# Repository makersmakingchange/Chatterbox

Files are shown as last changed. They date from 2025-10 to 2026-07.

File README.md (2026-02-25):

<!--- Open Source Assistive Technology: GitHub Readme Template Version 1.2 (2024-May-27)  --->

<!--- INSTRUCTIONS --->
<!--- This is a markdown template for creating the README.md file in a GitHub repository. This file is rendered and displayed automatically when someone visits the repository.

This document includes helper text that will not be displayed when rendered. Any text between the less-than sign + exclamation mark + three hyphen-minus (<!---) and matching three hyphen-minus + greater-than sign will not be displayed. This helper text can be deleted once the corresponding section is completed.

This template has a number of fields that can be searched and replaced with other text:
 - <Device_Name> Replace this with filename-friendly version of the device with underscores. e.g., Open_Wobble_Switch
 - <DeviceName> Replace this with the human-readable name of the device with spaces. e.g., Open Wobble Switch
 - <DesignerName> Replace this with the person or organization responsible for the design. e.g., John Doe.
 - <Repository_Link> Replace this with the web address for the repository. e.g., (e.g., https://github.com/makersmakingchange/Open-Wobble-Switch))
 - <MMCWebLink> This is the website address including an alphanumeric id for the Makers Making Change Website. e.g., 01tJR000000698oYAA. This will come from MMC staff.  
 - <MaterialCost> Replace this with the dollar cost and currency (CAD, USD, etc.) of the materials of the device.
 - <ShippingCost> Replace this with the dollar cost and currency (CAD, USD, etc.) of shipping the device (if possible).
 - <YEAR> year(s) of the copyright
 
Any text that is currently holding a space / is an instruction for the person filling in the README is in all capitals, to make it easier to see them in a rendered version.

--->
 
<!--- TITLE --->
# Chatterbox

## Overview
<!--- A brief summary of the project. What it does, who it is for, how much it costs. --->
The Chatterbox is an Augmented and Alternative Communication (AAC) device that allows users to play pre-recorded messages using single or dual switch scanning. The Chatterbox provides auditory and visual feedback to indicate the message a user can play. 

The Chatterbox is comprised of off-the-shelf electronics and 3D printed parts. 

The Chatterbox is open assistive technology (OpenAT). Under the terms of the open source licenses, the device may be built, used, and improved upon by anyone.

The overall cost of materials is about $135 CAD.

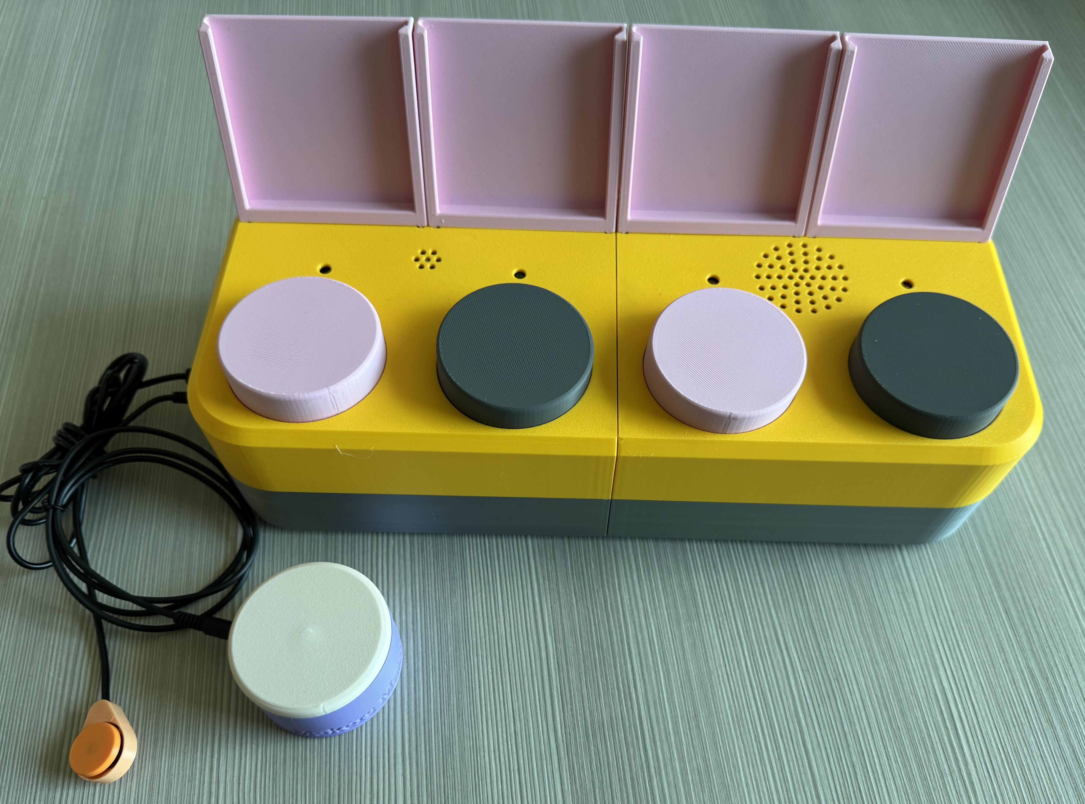
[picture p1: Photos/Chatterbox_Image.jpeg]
Picture of the Chatterbox.


## Makers Making Change Assistive Device Library
<MMCWebLink>

## How to Obtain the Device
### 1. Do-it-Yourself (DIY) or Do-it-Together (DIT)

This is an open-source assistive technology, so anyone is free to build it. All of the files and instructions required to build the device are contained within this repository. Refer to the Maker Guide below.

### 2. Request a build of this device

You may also submit a build request through the [Makers Making Change Assistive Device Library Listing](<MMCWebLink>) to have a volunteer maker build the device. As the requestor, you are responsible for reimbursing the maker for the cost of materials and any shipping.

### 3. Build this device for someone else

If you have the skills and equipment to build this device, and would like to donate your time to create the device for someone who needs it, visit the [MMC Maker Wanted](https://makersmakingchange.com/maker-wanted/) section.

## Build Instructions
<!--- Outline the major steps required to create a build --->

### 1. Read through the Maker Guide

The [Maker Guide](/Documentation/Chatterbox_Maker_Guide.pdf)  contains all the necessary information to build this device, including tool lists, assembly instructions, programming instructions (if applicable) and testing.

### 2. Order the Off-The-Shelf Components

The [Bill of Materials](/Documentation/Chatterbox_BOM.xlsx) lists all of the parts and components required to build the device.

### 3. Order the custom PCBS

The [PCB Files](/Build_Files/PCB_Build_Files) contain the Gerber files needed to order the PCBs, and instructions on how to order them can be found in the [Maker Guide](/Documentation/Chatterbox_Maker_Guide.pdf).

### 4. Print the 3D Printable components

All of the files and individual print files can be found in the [/Build_Files/3D_Printing_Files](/Build_Files/3D_Printing_Files/) folder.

### 5. Assemble the Chatterbox

Reference the Assembly Guide section of the [Maker Guide](/Documentation/Chatterbox_Maker_Guide.pdf) for the tools and steps required to build the device.

## How to improve this Device
As open source assistive technology, you are welcomed and encouraged to improve upon the design. 

## Files
### Documentation
<!--- Update the name, link, and version for documentation --->
| Document             | Version | Link |
|----------------------|---------|------|
| Design Rationale     | 1.0     | [Chatterbox_Design_Rationale](/Documentation/Chatterbox_Design_Rationale.pdf)     |
| Maker Guide          | 1.0     | [Chatterbox_Maker_Guide](/Documentation/Chatterbox_Maker_Guide.pdf)     |
| Bill of Materials    | 1.0     | [Chatterbox_Bill_of_Materials](/Documentation/Chatterbox_BOM.xlsx)     |
| User Guide           | 1.0     | [Chatterbox_User_Guide](/Documentation/Chatterbox_User_Guide.pdf)    |
| Changelog            | 1.0     | [Changelog](CHANGES.txt)     |

### Design Files
<!--- Include a copy of the original design files to facilitate easy editing and customization. Consider also including a generic format (e.g., STEP) --->
 - [CAD Files](/Design_Files/CAD_Design_Files)
 - [PCB Files](/Design_Files/PCB_Design_Files)

### Build Files
<!--- Include a copy of the build files intended for manufacturing. This may include svg files for laser cutting, stl files for 3d printing, Gerber files for custom PCBs, and Arduino files for custom firmware. --->
 - [3D Printing Files](/Build_Files/3D_Printing_Files)
 - [PCB Build Files](/Build_Files/PCB_Build_Files)
 - [Firmware Files](/Build/Firmware_Files)

## License
<!--- Add the year(s) for the copyright and the Designer Name. You may use the standard set of open licenses or choose your own for the hardware, software, and accompanying materials. --->
Copyright (c) 2025, Neil Squire.

This repository describes Open Hardware:
 - Everything needed or used to design, make, test, or prepare the Chatterbox is licensed under the [CERN 2.0 Weakly Reciprocal license (CERN-OHL-W v2) or later](https://cern.ch/cern-ohl ) .
 - All software is under the [GNU General Public License v3.0 (GPL-3.0)](https://www.gnu.org/licenses/gpl.html).
 - Accompanying material such as instruction manuals, videos, and other copyrightable works that are useful but not necessary to design, make, test, or prepare the <Device-Name> are published under a [Creative Commons Attribution-ShareAlike 4.0 license (CC BY-SA 4.0)](https://creativecommons.org/licenses/by-sa/4.0/) .

You may redistribute and modify this documentation and make products using it under the terms of the [CERN-OHL-W v2](https://cern.ch/cern-ohl).
This documentation is distributed WITHOUT ANY EXPRESS OR IMPLIED WARRANTY, INCLUDING OF MERCHANTABILITY, SATISFACTORY QUALITY AND FITNESS FOR A PARTICULAR PURPOSE.
Please see the CERN-OHL-W v2 for applicable conditions.

Source Location: [Chatterbox Repository](https://github.com/makersmakingchange/Chatterbox)

## Attribution
<!--- Provide any necessary attribution for designs or components that are included in the device or as part of the project. --->
The device was designed by Stephan Dobri for Neil Squire. It was based on the [Open Playback Recorder](https://github.com/makersmakingchange/Open-Playback-Recorder), from Neil Squire.

<!--- This is the attribution for the template. --->
The documentation template was created by Makers Making Change / Neil Squire Society and is used under a CC BY-SA 4.0 license. It is available at the following link: [https://github.com/makersmakingchange/OpenAT-Template](https://github.com/makersmakingchange/OpenAT-Template)

### Contributors
<!--- List the names of the people that contributed to the design. This could include the original source of the idea, designers, testers, documenters, etc. --->
Designers:
 - Stephan Dobri
 - Jake McIvor

Feedback providers:
- [SpikedCola](https://github.com/SpikedCola)

Testers:
 - Surrey School AAC Team
 - SET-BC
 - Augmented and Alternative Communication - Interaction and Technology Lab (AAC-IT) at Queen's University

---

<!-- ABOUT MMC START -->
## About Makers Making Change
[Makers Making Change Logo](https://www.makersmakingchange.com/)

Makers Making Change is a program of [Neil Squire](https://www.neilsquire.ca/), a Canadian non-profit that uses technology, knowledge, and passion to empower people with disabilities.

Makers Making Change leverages the capacity of community based Makers, Disability Professionals and Volunteers to develop and deliver affordable Open Source Assistive Technologies.

 - Website: [www.MakersMakingChange.com](https://www.makersmakingchange.com/)
 - GitHub: [makersmakingchange](https://github.com/makersmakingchange)
 - Bluesky: [@makersmakingchange.bsky.social](https://bsky.app/profile/makersmakingchange.bsky.social)
 - Instagram: [@makersmakingchange](https://www.instagram.com/makersmakingchange)
 - Facebook: [makersmakechange](https://www.facebook.com/makersmakechange)
 - LinkedIn: [Neil Squire Society](https://www.linkedin.com/company/neil-squire-society/)
 - Thingiverse: [makersmakingchange](https://www.thingiverse.com/makersmakingchange/about)
 - Printables: [MakersMakingChange](https://www.printables.com/@MakersMakingChange)

### Contact Us
For technical questions, to get involved, or to share your experience we encourage you to [visit our website](https://www.makersmakingchange.com/) or [contact us](https://www.makersmakingchange.com/s/contact).
<!-- ABOUT MMC END -->

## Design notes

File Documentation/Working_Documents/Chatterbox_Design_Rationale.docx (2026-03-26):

# Overview

The Chatterbox is a switch scanning communication device which provides auditory feedback to guide the user while scanning. The Design Rationale is intended to provide designers and maker information about the design process and design decisions behind the development of the Chatterbox.

Figure 1: The completed Chatterbox with assistive switches.

The Design Rationale details development chronologically. For full details on the current published version of the device, you may skip to the Detailed Design section.

# Introduction

The request for this device came from staff at a Surrey School District school for students with disabilities. The staff were looking for an affordable device to help students with visual impairment learn switch scanning for communication devices. The goal of the device is to help students trial switch scanning communication devices before purchasing a more expensive commercial option. The device requires auditory feedback as it is intended for users with visual impairment, and many commercially available options use visual feedback for switch scanning.

The device allows users to record their own messages to play back when selected using switch scanning, or direct selection of a message. Messages can range from single words to full sentences or sections of songs. The messages allow users who have complex communication needs to interact with other people and participate in group activities. The simplicity of the device helps teach users about switch scanning, before using more complex switch scanning communication devices.

The device is intended for users with complex communication needs and visual impairments, including users who are deaf-blind, blind, visually impaired, or have cerebral palsy (CP).

# Requirements

## Problem Statement

Design an OpenAT device that enables a user with visual impairment to perform switch-enabled auditory scanning.

## User Needs

G01 | A switch scanning communication device that uses auditory feedback for switch scanning.
G02 | Device is simple to help teach users how to switch scan rather than learning how to use the device.
G03 | Has integrated switches to directly play and record messages.
G04 | The device can do single and perhaps dual switch scanning.
G05 | The volume of the device can be controlled.
G06 | The delay between scanning messages can be controlled.
G07 | The device can hold images on paper near each switch to represent the message.
G08 | The device can record and play at least three messages.
G09 | The device is more affordable than current commercially available options.
G10 | The device is small enough to fit on a user’s lap tray.
G11 | The device has different message levels to store and playback sets of messages.
G12 | The device shows which level it is on.
G13 | The device shows which message is being played/recorded.
G14 | The device must be able to clean.
G15 | Integrated buttons should not be angles
G16 | It should be easy to record messages.

## Functional Requirements

F01 | Secondary users must be able to record their own messages.
F02 | Messages up to a minute in length must be possible to record.
F03 | The device must record at least three separate messages.
F04 | The device must work with single switch scanning.
F05 | Users must be able to add message labels or pictures to help identify the messages (76x76 mm minimum size).
F06 | The delay between messages while switch scanning can be modified.
F07 | The volume of the playback must be adjustable by a secondary user.
F08 | The device must be able to be cleaned with a damp cloth.
F09 | The device must fit on a student’s lap tray (maximum length 330 mm).
F10 | The device must be able to record and play at least two different levels of messages.
F10a | The device must have a means to change the level.
F10b | The device must have a way to indicate the current level.
F11 | Integrated buttons on the device must be parallel to the surface the device is mounted or placed upon.
F12 | The device enables switch-enabled auditory scanning
F12a | The device plays pre-recorded messages when triggered by primary user.
F12b | The device must be able to record a message for each position.
F12c | The device must have a visual indicator for each position.
F12d | The device must have a means for indicating the current position.
F12e | The device must play a selected message again when selected by the user.
F13 | The device must have a way to indicate which position is being recorded.

## Evaluation Criteria

NF01 | The device should have separate jacks for connecting external assistive switches for direct access.
NF02 | The device should provide an option for two-switch scanning.
NF03 | The device should have integrated buttons for direct access
NF04 | The device should have visual feedback for secondary users, or users with partial vision.
NF05 | The device should have the option to have integrated buttons with different tactile tops.

## Constraints

C01 | The device must cost less than other commercially available options ($300 CAD).
C02 | The device must be makeable by a volunteer.
C03 | Any required custom printed circuit boards (PCBs) are makeable through low-volume prototyping services.
C04 | The device design must be licensed as open source hardware.

# Research

Research on existing devices was conducted between September 10th and 18th, 2024. Research was conducted by searching Google for “auditory scanning devices”, “switch scanning devices”, and using “DIY”, and “homemade” with the previous searches. The augmented and alternative communication (AAC) team that requested this device also suggested commercially available devices as starting points for the design.

## Background

Simple switch scanning AAC devices are used by people with complex communication needs and limited motor function. Messages are often short (single words or short statements), but may be longer depending on the user’s needs and the context of the use.

## Commercially Available Options

Options that can be purchased but not made by a maker.

### AbleNet Inc. Talking Brix 2

Title / Name of device | Talking Brix 2
Link | https://www.ablenetinc.com/talkingbrix-2/
Author | AbleNet Inc.
License | N/A
Cost | $365.00 CAD

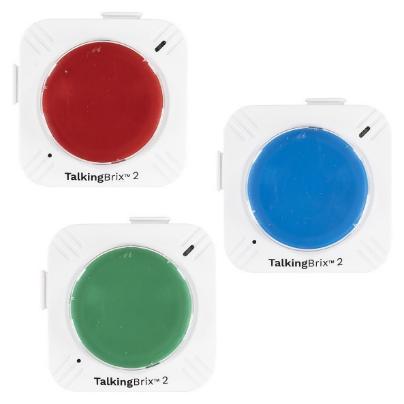
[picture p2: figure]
Three AbleNet Talkig Brix. They are white squares with indicator lights and a circular red, green, or blue button on them.

Figure 2: Set of three Talking Brix 2 devices.

The Talking Brix 2 come in sets of three individual playback buttons. Each button works separately, can record up to 10 seconds of audio, and have rechargeable batteries. To record messages, the user moves a switch on the bottom of the base to “Rec” and holds the Brix button down while recording the message. When the switch is turned to “On”, the recorded message will play when the button is pressed. The Brix can be physically connected using the slots and tabs on the sides; however, these connections are for physical mounting only and each Brix will still need to be pressed to be activated.

Requirements Met | Requirements Unmet
F01, F03 | F02, F04-F07

#### Useful Design Features

The tabs and slots on the sides of the Brix to connect them are well made. There are also push pins on the tabs which appear to be useful for creating electrical communication among the Brix, although they are unused in this design.

Each Brix has a magnet in the bottom to allow for mounting on metal surfaces.

### Cheap Talks 4 & 8 – Direct Scan and Jacks

Title / Name of device | Cheap Talks 4 & 8 – Direct Scan and Jacks
Link | https://enablingdevices.com/product/cheap-talks-4-8-direct-scan-jacks/
Author | Enabling Devices
License | N/A
Cost | $319.95 – $339.95 (USD)

Figure 3: Cheap Talks 4 - Direct Scan and Jacks

The Cheap Talks 4 & 8 – Direct Scan and Jacks can record and replay either four (4) or eight (8) messages. Messages can be up to 37.5 seconds in length on each button. The device supports single or dual switch scanning with external switches in eight (8) scanning modes. Users can also press the buttons on the device to directly select one of the messages to play.

Users record messages by holding the “Record” button and intended message button down simultaneously. Dials and buttons on the back allow users to change the volume, scanning speed, and scanning mode.

Requirements Met | Requirements Unmet
F01, F03, F04, F07 | F02, F05, F06

#### Useful Design Features

Options of multiple scanning methods (https://enablingdevices.com/wp-content/uploads/2017/09/Scan-Modes.pdf) are useful and described well.

The buttons also light up when playing messages or other auditory cues for scanning.

### Talk 4 with Levels

Title / Name of device | Talk 4 with Levels
Link | https://enablingdevices.com/product/talk-4-wlevels/
Author | Enabling Devices
License | N/A
Cost | $299.95 (USD)

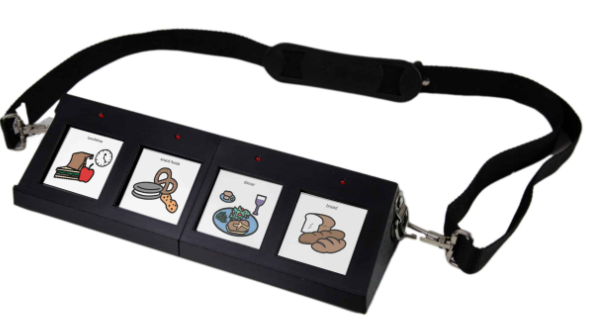
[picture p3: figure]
A black device with a lanyard and four buttons. The buttons are square and have images of types of food on them.

Figure 4: Talk 4 with Levels

The Talk 4 is like the Cheap Talks, but only has one jack for switch scanning. It is a more portable version, with 12 levels of messages, and up to 300 seconds of memory for recorded messages.

Requirements Met | Requirements Unmet
F01, F03, F04 | F02, F05-F07

#### Useful Design Features

Levels are useful for increasing the number of possible messages.

### Announcer with 6 Levels

Title / Name of device | Announcer with 6 Levels
Link | https://enablingdevices.com/product/announcer-w6-levels/
Author | Enabling Devices
License | N/A
Cost | $339.95 (USD)

Figure 5: Announcer with 6 Levels

The Announcer has six (6) levels of messages, with 300 seconds of message recording time. The Announcer has a built-in switch and mounting clamp, and can be activated with an external switch. The beginning of messages are played at a lower volume than the messages when selected/played back.

Requirements Met | Requirements Unmet
F01, F02, F03 | F04, F05-F07

#### Useful Design Features

Playing the message cue at a lower volume than the message may be useful.

### Tech Scan and Smart Scan Devices

Title / Name of device | Tech Scan and Smart Scan Devices
Link | https://www.turningpointtechnology.com/Comm/Auditory.asp
Author | Turning Point Technology
License | N/A
Cost | $1,018 - $2,450 USD

Figure 6: Tech Scan Device

The Tech Scan and Smart Scan devices are direct and switch scanning devices with different numbers of messages. The devices have either eight (8) or 32 messages/square for message selection. Each device also has multiple levels for more messages, and standard message length is 4.5 seconds.

Requirements Met | Requirements Unmet
F01, F03 | F02, F04, F05-F07

#### Useful Design Features

No new design features other commercially available options haven’t included.

### Talk About! Communicator

Title / Name of device | Talk About! Communicator
Link | https://www.adaptivetechsolutions.com/pd-talk-about-communicator/?srsltid=AfmBOoq3FJIaj412QSOrk76TpdaQk041moJlEOmOddBrGyGvxO57XSLE
Author | Adaptive Tech Solutions
License | N/A
Cost | $27.58-$37.83 (USD)

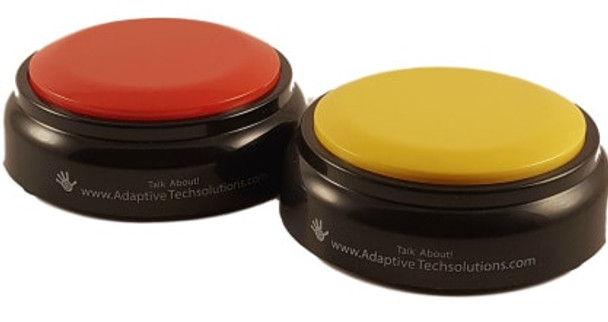
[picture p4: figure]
Talk About! Communication Talking Buttons

Figure 7: Two Talk About! Communicators

Records and plays back messages up to 20 seconds long. Includes non-slip pads on the bottom, and there is a switch jack version for use with external switches. Additionally has a belt clip so make it wearable/portable.

Requirements Met | Requirements Unmet
F01 | F02-F07

#### Useful Design Features

Can be used with an external switch, and option for belt clip is interesting.

### iTalk 4

Title / Name of device | iTalk 4
Link | https://www.ablenetinc.com/italk4/
Author | AbleNet, Inc.
License
Cost | $275 (USD)

Figure 8: iTalk 4 device

The iTalk 4 offers four individual messages with three message levels (12 messages total) with a total of six (6) minutes of recording time. Each button corresponds to a message, and each message can be recorded independently. External switches can be used for each message; however, there is not a switch scanning mode.

Requirements Met | Requirements Unmet
F01, F03 | F02, F04-F07

#### Useful Design Features

Individual recording of each message is useful, as are the levels.

### Compartmentalized Communicators

Title / Name of device | Compartmentalized Communicators
Link | https://enablingdevices.com/product/compartmentalized-communicators/?srsltid=AfmBOoqLPBpBhjRKIVVAHyzmXBPQkFkR4kDSdKowHBe27DFtp3_HjVcO
Author | Enabling Devices
License
Cost | $179.95 - $269.95 (USD)

Figure 9: Compartmentalized Communicators in 2, 3, and 4 compartment versions.

The Compartmentalized Communicator has two-, three-, or four-compartment versions. Each compartment can record up to a five (5) second message that is played back when the plate is pressed. There are spaces for images and objects to be placed above each compartment. There is no switch scanning option.

Requirements Met | Requirements Unmet
F01, F03, F07 | F02, F04-F06

#### Useful Design Features

Having space for both an object and an image may be useful.

Having the switches flat (not angled) makes it easier for some users to press.

## DIY / Maker-Friendly Options

Options that can be made by a maker.

### Partner – Assisted Auditory Scanning (PAAS)

Title | Partner – Assisted Auditory Scanning
Link | https://communication.bridgeschool.org/intervention/aac-system-design-guiding-principles/aac-system-design-examples-of-aac-tools-and-techniques/
Author | N/A
License | N/A
Cost | N/A
Test Build (Y/N) | N/A
Add to Library (Y/N) | N/A

Partner-Assisted Auditory Scanning relies on a partner going through a series of options verbally, and having the user select from the choices they present. The series of options can be developed by anyone, and can be presented in various ways (pictures, words, etc.).

Requirements Met | Requirements Unmet
None | F01-F07

### Open Playback Recorder

The Open Playback Recorder is an open-source device that can record three lists of voice messages that its user can playback via the trigger of an accessible button connected through a 3.5 mm mono jack. It aims to assist users with communication difficulties by giving them alternative methods to engage in conversation. This device has functionality like AbleNet’s Big Mack or Step by Step.

Title | Open Playback Recorder
Link | https://www.makersmakingchange.com/s/product/open-playback-recorder/01tJR000003DNOVYA4
Author | Neil Squire/Makers Making Changes
License | CERN OHL-W v2, GPL-3.0, CC BY SA 4.0
Cost | $90 (CAD)
Test Build (Y/N) | Y
Add to Library (Y/N) | Already in library

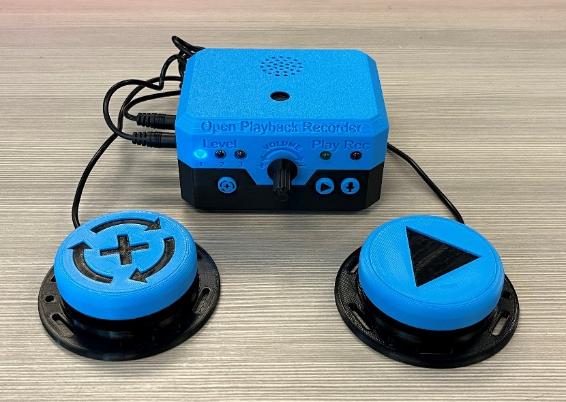
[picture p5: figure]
Picture of Open Playback Recorder.

Figure 10: Open Playback Recorder

The Open Playback Recorder allows users to record and switch scan messages to engage in communication. There are three levels to record different messages, and users record a series of messages on each level. Recording, switching levels, and scanning messages can all be done using assistive switches, or built-in switches on the device.

Messages cannot be modified or accessed directly; users must re-record all messages on a level at once, and must switch scan to access messages.

Requirements Met | Requirements Unmet
F01-F04, F07 | F05, F06

#### Useful Design Features

Most of the components and firmware from this device can be used as the basis for the Auditory Scanning Blocks device.

### Single Message Playback Switch

The Single Message Playback Switch is a switch adapted device that can store and play back a single 30 second message. The device can be used both as a toy or as a communication aid. A commercially available voice recording button is modified so that it can be activated using a secondary assistive switch with a 3.5 mm plug.

Title | Single Message Playback Switch
Link | https://www.makersmakingchange.com/s/product/single-message-playback-switch/01tJR000001HyonYAC
Author | Neil Squire/Makers Making Changes
License | CERN OHL-W v2, GPL-3.0, CC BY SA 4.0
Cost | $12.50 (CAD)
Test Build (Y/N) | Y
Add to Library (Y/N) | Already in library

Figure 11: Single Message Playback Switches

Requirements Met | Requirements Unmet
F01, F03 | F02, F04-F07

#### Useful Design Features

The useful functions are the same as the Talking Brix 2.

# Ideation

## I01 - Push pins for electrical connection

Use electrical push pins for the electrical connections among the individual blocks, like the Talking Brix 2 have. These pins wouldn’t help with the physical connection among the blocks, so would require a strong physical connection, like the Talking Brix 2 sliding and locking together.

## I02 - Modifying Open Playback Recorder

Start with the firmware and electrical components of the Open Playback Recorder, and modify them as needed to meet the unmet functional requirements. The firmware will require minimal changes to adjust how messages are recorded and played back. Some components will be removed, some added, and the custom PCB will need to be redesigned for different functions and form factor.

Modification would include:

- Change in size and shape to meet client’s needs
- Removing external switch access to record and level changes
- Adding direct access to record messages instead of levels
- Adding internal switches for direct access to each message
- Adding option to change delay between messages while switch scanning
- Add ability to use two-switch scanning

## I03 - Array of Single Message Playback Switches

The Single Message Playback Switches already include recording, playback, and direct access control. An array of them could be controlled with a microcontroller to allow switch scanning across the single message switches.

Using the array would be cheap and straightforward to implement, but would limit recording time, not allow message levels, or control over volume.

## I04 - Using mechanical keyboard switches for direct selection buttons

Mechanical keyboard switches come with many options for activation force and feedback style, so they are an interesting option for making customizable switches. Designing a device to be hot swappable (be able to change keyboard switches without soldering) allows users to easily customize their switch.

The simplest way to make a switch hot swappable is to add a hot-swap socket (https://www.digikey.ca/en/products/detail/mill-max-manufacturing-corp./3305-0-15-80-47-27-10-0/13901970?productid=13901970&gad_source=1) to a PCB. The socket must be soldered in, but it allows the keyboard switch to be inserted and changed without additional soldering. SparkFun created an open-source breakout board (https://github.com/sparkfun/Cherry_MX_Switch_Breakout) for Cherry MX switches (https://www.cherry.de/en-gb/products/mx-switches).

## Ideation Decisions

Idea | Decision (Abandon, Modify, Proceed) | Justification
I01 - Push Pins | Abandon | The requestors did not need a modular device.
I02 – Modified Open Playback Recorder | Proceed | This option would allow us to meet all the requirements of the requestors.
I03 – Array of single messages | Abandon | This option meets most of the requirements of the requestor and will likely be the most affordable option; however, the requestors stated they must have multiple message levels.
I04 – Mechanical keyboard switches | Abandon | While a useful option for other projects, the customization option was not necessary for this project.

# Conceptual Designs

## Use Cases

Different use cases were created to help guide the concept development, prototyping, and design. These use cases account for end-users with different levels of ability, and secondary users who are recording messages and selecting levels. These use cases were informed by conversations with the original requestors of the device.

### General use flow

The general use goes through the initial setup through to use by a primary user. Each user scenario/use case is described in detail following the flow diagram.

Turn device on
Check level
Check if messages are recorded
Enter record mode
Record messages
Exit record mode
Add image cards above switches
Plug in assistive switch(es)
Start switch scanning
Advance message
Select message
Turn off device
Decide if single or dual switch scanning
Exit switch scanning

Figure 12: Flow chart of general use of the Chatterbox.

### Single switch scanning

The device will need to be able to play messages with single switch scanning. Users can press an assistive switch to start the device scanning through the messages (playing either a part of a message, or the whole message) and press it again to select and play a message. Regardless of the ability of an end-user they will need to:

- Initiate switch scanning with their assistive switch
- Hear the auditory feedback
- Have time to process the auditory feedback and decide if it is the message they would like to select
- Use their assistive switch to select a message

#### End-user with partial sight

An end-user with partial sight will be able to receive auditory and some visual feedback. It could be useful for them to receive visual feedback to indicate which message is currently being played and will be selected if they activate their switch.

#### End-user without sight

An end-user without sight would rely solely on the auditory feedback from the device to know which message will be played when they activate their assistive switch.

### Double switch scanning

Double switch scanning allows users to activate one switch to advance through scanning options and the other to select an option. Users will need to:

- Initiate switch scanning with their assistive switch
- Hear the auditory feedback
- Have time to process the auditory feedback and decide if it is the message they would like to select
- Use a second assistive switch to advance to the next option once they know if they would like to select the current option
- Use a second assistive switch to select their desired message when it is available

### Directly choosing to play a message instead of switch scanning

A primary or secondary user can press one of the direct access switches to play a message directly.

- Select which message to play back
- Press direct access switch to play message

### Secondary users recording messages

Secondary users recording messages are assumed to not have severe disabilities. Switches can be small, and feedback can come through any modality. Secondary users will need to be able to:

- Switch the device to record messages
- Confirm the device is in record mode
- Select the level to record on
- Confirm which level the device is recording on
- Select the message to be recorded
- Confirm which message is being recorded
- Record message
- Exit recording mode
- Playback message to confirm it is correct

Secondary users will be the only ones recording messages and changing levels.

### Secondary users observing an end-user

A secondary user may want to observe and help the primary user when learning the device. While doing so, it would be useful for them to know which message is being played at different times.

- Break into flow of initial setup to end-user using device
  - User story flow

### Secondary users changing image cards for messages

A secondary user may switch the image cards out to represent what each message means on a set level.

- Identify the level the device is set to
  - Change level if necessary
- Identify the messages on each switch
  - Record new messages if necessary
- Place image cards above each switch to represent the message

Only secondary users are expected to change the image cards.

Three initial concepts were created for the device. All three concepts used existing devices on the MMC website as the base for the designs.

## Concept 1: Single Message Playback Switch Array

Single Message Playback Switches (https://www.makersmakingchange.com/s/product/single-message-playback-switch/01tJR000001HyonYAC) are mounted together and can be controlled through single or two-switch scanning. A sketch of the array is below:

Figure 13: Sketch of Concept 1 of the Chatterbox.

Concept 1 would hold the voice recording buttons from the Single Message Playback Switch to record and play back messages. A microcontroller would be added to allow single or two-switch scanning across the voice recording buttons. Each switch and the microcontroller would need batteries, and the microcontroller would be turned on and off with a switch on the back of the device. Ports for accessing the microcontroller and attaching the external switches for scanning would be on the side of the device.

Users could use external assistive switches to switch scan across the voice recording buttons, or press the buttons to directly select and play back a message.

A cardboard mock-up was also created to get a better idea of the size and shape of this design. Note that there were only three buttons shown in the cardboard mock-up. This was because of the size limitation on the length of the device; four buttons with clearance between them would have been wider than the maximum length.

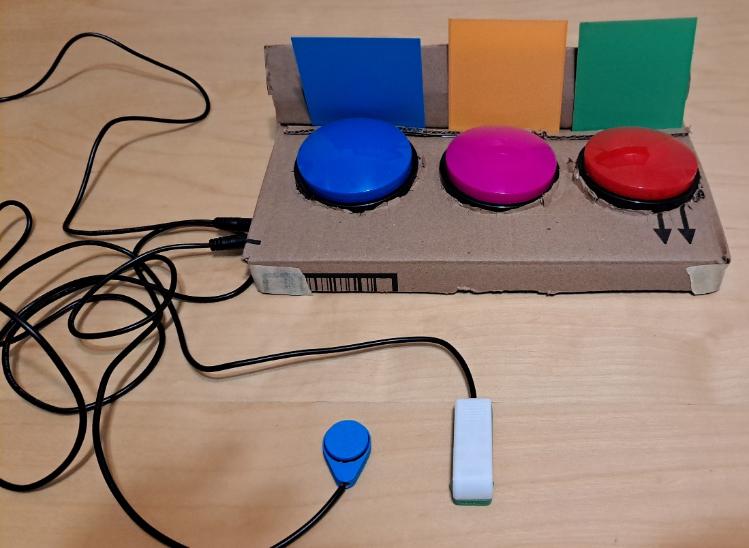
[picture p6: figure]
A cardboard mock-up of the single message playback switch array.

Figure 14: Cardboard mock-up of Concept 1.

### Physical Component / Enclosure

Concept 1 would consist of a 3D printed enclosure to surround the voice recording buttons (https://www.amazon.ca/gp/product/B09V1JJ3D1/ref=ppx_yo_dt_b_asin_title_o00_s00?ie=UTF8&psc=1) and house the electrical components of the device. The enclosure would include a slot behind the voice recording buttons to allow caregivers/secondary users to place images behind the switches to represent the message that will be played.

Due to the size constraint of the design, only three buttons could be mounted together this way.

### Electrical Components

Concept 1 would require three voice recording buttons, a microcontroller, LEDs, resistors, and switch jacks for the external switches. This concept would likely be simple enough not to require a custom PCB.

### Code Structure / Function

The code would only be used to control switch scanning with these buttons as any recording and playback of the messages is already handled in the voice recording buttons.

The general flow of the code is demonstrated in the figure below.

## Concept 2: Modified Open Playback Recorder – Direct Message Access

A single or two-switch scanning device with auditory feedback to play pre-recorded messages. Users can switch scan to find messages, or press switches directly linked to each message.

Figure 15: Sketch of Concept 2 of the Chatterbox.

A cardboard mock-up was also created for this version of the device.

Figure 16: Cardboard mock-up of Concept 2.

### Physical Component / Enclosure

Concept 2 would consist of a 3D printed enclosure to house the electrical components of the device. The enclosure would include a slot behind the direct access switches to allow caregivers/secondary users to place images behind the switches to represent the message that will be played. The direct access switch toppers would be designed so they could be switched easily (without the need of external fasteners). The ease of switching toppers would allow secondary users to replace toppers with ones that represent what each message played, or with textures to help users differentiate between the switches.

The enclosure would be 3D printed in multiple parts to make assembly and repair easier.

### Electrical Components

Concept 2 would include the electrical components from the Open Playback Recorder, with any additional components required for the differences in functions. These parts would include two three-position switches to change levels and playback speed, and custom PCBs to make assembly easier.

### Code Structure / Function

The code would function as outlined in flow diagram below.

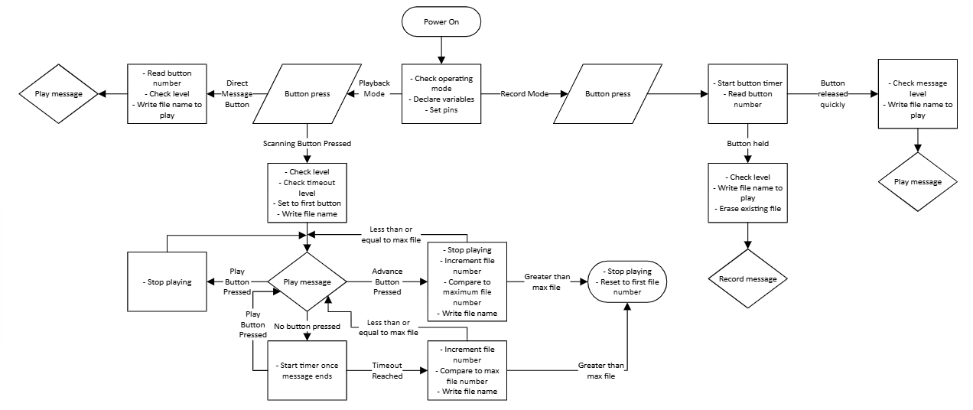
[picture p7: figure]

Figure 17: Flowchart of how the code functions for Concepts 1 and 2.

## Concept 3: Modified Open Playback Recorder – No Direct Message Access

A single or two-switch scanning device with auditory feedback to play pre-recorded messages.

Figure 18: Sketch of Concept 3 of the Chatterbox.

The cardboard mock-up for this design was the smallest, as it did not require space for integrated direct-access message.

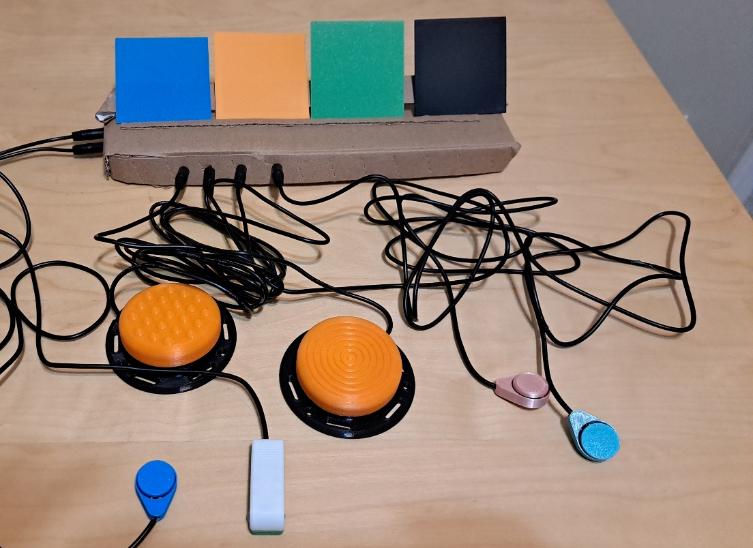
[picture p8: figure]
A cardboard mock-up of the chatterbox version without integrated direct access message buttons. To access/record each message, users would need to plug in additional assistive switches.

Figure 19: Cardboard mock-up of Concept 3.

### Physical Component / Enclosure

This concept has the same general enclosure and physical components as Concept 2, but the user would require four additional assistive switches to access each message directly. These assistive switches would take the place of the four built-in switches in Concept 2.

### Electrical Components

This concept has the same general parts as Concept 2, except the switches required for the built-in switches.

### Code Structure / Function

The code would function exactly as the code in Concept 2.

## Concept Decisions

Concept | Decision (Abandon, Modify, Proceed) | Justification
Concept 1: Single Message Playback Switch Array | Abandon | The requestors needed levels and volume control as part of the design.
Concept 2: Modified Open Playback Recorder – Direct Messages Access | Proceed | The requestors thought this version best met their needs.
Concept 3: Modified Open Playback Recorder – No Direct Messages Access | Abandon | The requestors preferred having direct access to each message integrated with the device to focus it on teaching switch scanning.

# Prototyping

Two prototypes were created: a solderless breadboard for testing the code and hardware, then a soldered protoboard version with a 3D printed enclosure. The soldered version with an enclosure was sent to two groups in Kingston, Ontario to test.

## Solderless Breadboard

The solderless breadboard prototype was used to build out the physical components and test the code of the Chatterbox. The solderless breadboard version started as the Open Playback Recorder schematic, and was modified throughout the prototyping process.

Figure 20: Solderless breadboard prototype of the Chatterbox.

### Goals for this prototype:

The solderless breadboard prototype was meant to fully develop the code and the electronic components required for the Chatterbox. This prototype was meant to provide a proof of concept and function before putting in the time and resources to design a custom PCB.

The goals of the prototype were to:

- Test the audio recording and playback
- Develop and test the methods to change playback speed
- Develop and test the methods to change the message level
- Develop and test how users receive feedback from the device
- Develop and test the single switch scanning mode
- Develop and test the dual switch scanning mode
- Develop and test the method to record new messages

### Electrical Components

The electronic components in this prototype were mostly from the Open Playback Recorder, with a few added parts. The solderless breadboards and jumper wires were not included in the list of parts below.

Part | Quantity | Cost (CAD) | Link
Seeeduino Nano | 1 | $7.60 | https://www.digikey.ca/en/products/detail/seeed-technology-co-ltd/102010268/10290292
5V ready micro SD breakout board | 1 | $7.50 | https://www.digikey.ca/en/products/detail/adafruit-industries-llc/254/5761230
2.5W Class D amp | 1 | $3.95 | https://www.digikey.ca/en/products/detail/adafruit-industries-llc/2130/5761279
2.2 kOhm resistor | 12 | $1.20 ($0.10 each) | MFR-25FRF52-2K2 YAGEO | Resistors | DigiKey (https://www.digikey.ca/en/products/detail/yageo/MFR-25FRF52-2K2/13921897?gclsrc=aw.ds&gad_source=1&gad_campaignid=17336435733)
5mm LED | 4 | $0.96 ($0.24 each) | 151051BS04000 Würth Elektronik | Optoelectronics | DigiKey (https://www.digikey.ca/en/products/detail/w%C3%BCrth-elektronik/151051BS04000/4490009)
Mono speaker | 1 | $3.95 | 3351 Adafruit Industries LLC | Audio Products | DigiKey (https://www.digikey.ca/en/products/detail/adafruit-industries-llc/3351/6612456)
Potentiometer | 1 | $1.82 | PTN16-A10125K1A2 Same Sky (Formerly CUI Devices) | Potentiometers, Variable Resistors | DigiKey (https://www.digikey.ca/en/products/detail/cui-devices/PTN16-A10125K1A2/20380750)
Micro SD card | 1 | $4.95 | 5252 Adafruit Industries LLC | Memory - Modules, Cards | DigiKey (https://www.digikey.ca/en/products/detail/adafruit-industries-llc/5252/15841478)
Microphone | 1 | $7.95 | 1713 Adafruit Industries LLC | Development Boards, Kits, Programmers | DigiKey (https://www.digikey.ca/en/products/detail/adafruit-industries-llc/1713/4990777)
Tactile switch | 6 | $1.62 ($0.27 each) | B3F-4050 Omron Electronics Inc-EMC Div | Switches | DigiKey (https://www.digikey.ca/en/products/detail/omron-electronics-inc-emc-div/B3F-4050/95200)
3 position slide switch | 2 | $2.42 ($1.21 each) | OS103011MA7QP1 C&K | Switches | DigiKey (https://www.digikey.ca/en/products/detail/c-k/OS103011MA7QP1/1981432)
2 position slide switch | 2 | $1.90 ($0.95 each) | OS102011MA1QS1 C&K | Switches | DigiKey (https://www.digikey.ca/en/products/detail/c-k/OS102011MA1QS1/1981431)

### Code Structure / Function

The code for this prototype is built off the code for the Open Playback Recorder (https://github.com/makersmakingchange/Open-Playback-Recorder). The general code structure is outlined in this section.

#### Startup

- Check if in playback or record mode
  - Check the voltage on a pin (either pulled up or pulled down, depending on position of a three-position switch)
- Playback mode
  - All message LEDs are off unless message is being played
  - Wait for direct access switch to be pressed, or switch scanning to be started
    - If direct access switch pressed
      - Read message number based on switch number (pin pressed)
      - Check level
        - Level is controlled by voltage reading on a three-position switch and resistor ladder
      - Play corresponding message function
    - If switch scanning started
      - Check level
      - Light corresponding LED while message is playing
      - Play message in position 1
      - Check delay time
        - Delay time is controlled by voltage reading on a three-position switch and resistor ladder
        - Wait for delay time
      - If selection switch is not pressed during delay time, advance message and repeat
      - If selection switch is pressed at any time during delay or message playing
        - Replay current message
        - Exit switch scanning
      - If advance message switch is pressed at any time during playback
        - Stop playback
        - Advance to next message
        - Play next message
        - If advancing past the last message, start at first message again
      - If last message is reached and delay times out without any advance or selection
        - Exit switch scanning
- Record mode
  - Blink lights on all messages while no message is being recorded
  - Wait for direct access switch to be held
    - Stop blinking all lights
    - Read message number based on switch number (pin pressed)
    - Check level
    - Erase existing corresponding message
    - light on corresponding message when ready to record message (and while recording)
    - Record message while switch is being held
    - Stop recording when switch is released
    - Start blinking all four message lights again
  - Direct access switch is pressed, but no held
    - Stop blinking all lights
    - Read message number based on switch number (pin pressed)
    - Check level
    - Turn on corresponding LED
    - Play recorded message
    - Start blinking all four message lights again
  - Exit record mode

#### Functions

##### Check level

Level is controlled via analogue reading on a single pin connected to a three-position switch and a resistor network. The position of the switch will change the voltage reading on that single pin.

- Read the voltage on the analogue pin
- Compare voltage to two threshold values
  - If above top threshold, level 1
  - If between thresholds, level 2
  - If below lowest threshold, level 3

##### Check delay

The delay between messages ending and advancing to the next message is controlled in the same way as the level, using the same resistor network but a different three-position switch.

- Read the voltage on the analogue pin
- Compare voltage to two threshold values
  - If above top threshold, fast
  - If between thresholds, medium
  - If below lowest threshold, slow

The delays for slow, medium, and fast were chosen as 20 seconds, 15 seconds, and 10 seconds. These values are currently arbitrarily chosen but will be changed based on user feedback. There will also be instructions to change these delays in the code if a user/clinic decides they would like custom speeds.

##### Play message

The change to this function from the Open Playback Recorder will be that the message number does not update when the message plays, but is controlled by the end of the delay, or pressing the advance button switch. Additionally, the LED for the corresponding message will be on while playing

- Check level
- Read message number
- Turn on corresponding LED
- Play message
- Stop message playing

##### Record message

The record message function changes from the Open Playback Recorder with the introduction of direct message access. The messages on the level won’t all be deleted when entering record mode, but instead will be deleted individually when a new message is about to be recorded.

- Read the message being recorded
- Stop flashing all message lights
- Check the level
- Delete corresponding existing message
- Flash corresponding message LED
- Record message while switch is held
- Start flashing all message LEDs when message has been saved and ready to record new message

##### Switch scanning

The switch scanning function is only available in playback mode. The switch scanning is set for automatic switch scanning, where the user presses a switch to start scanning and select messages. Messages advance based on a pre-set delay period after the message has been played (as explained in the Check delay function). If a user has a second switch and would like to do dual switch scanning, a second switch can be used to advance to the next message at any time; however, the delay will still be in effect. If a user is dual switch scanning but does not select to replay or advance the message before the delay expires, the next message will play.

- Selection switch is pressed to initiate scanning
- Set message number as first message
- Play message function
- Wait for delay
- If no other input and delay expires
  - Turn off corresponding LED
  - Advance message number
  - Play next message
- If message is selected
  - Play message function again
- If advance message switch is pressed
  - Stop playing message
  - Advance message number
  - Check if message number is beyond number of messages
    - If beyond number of messages
      - Restart at first message
  - Play message function
- If last message is reached and delay expires on it without additional input
  - End message scanning

### Function and number of pins

The table below summarizes the function and pin type required for each part of the code.

Function | Number of pins | Type of pins
Button 1 LED | 1 | Analog or digital output
Button 2 LED | 1 | Analog or digital output
Button 3 LED | 1 | Analog or digital output
Button 4 LED | 1 | Analog or digital output
On/Off LED | 1 | Analog or digital output
Button 1 switch | 1 | Digital input
Button 2 switch | 1 | Digital input
Button 3 switch | 1 | Digital input
Button 4 switch | 1 | Digital input
Scanning switch jack | 1 | Digital input
Selecting switch jack | 1 | Digital input
Level selection (resistor array) | 1 | Analog input
Amp | 1 | Digital output
SD reader | 4 | Digital I/O
Microphone | 1 | Analog I/O
Audio potentiometer | 1 | Digital output
Record vs play state | 1 | Digital I/O

The total number of pins in this setup is 20.

### Microcontroller and peripherals comparison

The microcontroller inherited from the Open Playback Recorder was near its memory limit for the Open Playback Recorder, so other options were investigated. These options also included shields, which could simplify the circuitry and potentially decrease cost. The different microcontroller and peripherals comparisons are summarized in the following tables. To simplify the tables, common parts among the different options (such as the speaker and microphone) are excluded.

Seeeduino Nano and breakout boards (from Open Playback Recorder)
Part | Cost (CAD) | Link
Seeeduino Nano | $7.60 | https://www.digikey.ca/en/products/detail/seeed-technology-co-ltd/102010268/10290292
5V ready micro SD breakout board | $7.50 | https://www.digikey.ca/en/products/detail/adafruit-industries-llc/254/5761230
2.5W Class D amp | $3.95 | https://www.digikey.ca/en/products/detail/adafruit-industries-llc/2130/5761279

Note that the Feather boards are designed to be powered via USB or LiPoly batteries, not other methods like 9V batteries. A USB charger was added to the cost for these options to reflect this.

Adafruit Feather and Music Wing
Part | Cost (CAD) | Link
Adafruit Feather RP2040 | $11.95 | https://www.digikey.ca/en/products/detail/adafruit-industries-llc/4884/14000603
Music Maker FeatherWing with amp | $24.95 | https://www.digikey.ca/en/products/detail/adafruit-industries-llc/3436/6827175
USB charger | $14.95 | https://www.adafruit.com/product/1959

Adafruit Feather only
Part | Cost (CAD) | Link
Adafruit Feather RP2040 Adalogger | $14.95 | https://www.digikey.ca/en/products/detail/adafruit-industries-llc/5980/24639131
2.5W class D amp | $3.95 | https://www.digikey.ca/en/products/detail/adafruit-industries-llc/2130/5761279
USB charger | $14.95 | https://www.adafruit.com/product/1959

Adafruit ItsyBitsy M0 Express
Part | Cost (CAD) | Link
Adafruit ItsyBitsy M0 Express | $11.95 | https://www.digikey.ca/en/products/detail/adafruit-industries-llc/3727/8346575
5V ready micro SD breakout board | $7.50 | https://www.digikey.ca/en/products/detail/adafruit-industries-llc/254/5761230
2.5W Class D amp | $3.95 | https://www.digikey.ca/en/products/detail/adafruit-industries-llc/2130/5761279

Based on the increased cost and complexity of changing the microcontroller, we decided to continue using the Seeeduino Nano. The code had to be optimized to reduce memory usage due to the memory limitations of the Nano’s microchip.

### Memory usage optimization

Message playback was affected by memory limitations on the microchip. Once a certain memory threshold was reached (the exact value was not determined), the device would no longer play back messages. The device treated each message as if it were a very short recording without any sound, but functioned as expected otherwise. It was initially unclear what was causing the issues, but after testing other potential causes, it was determined that memory was the cause.

Most of the memory optimization came from changing the format of the debugging serial information. Initially, set character strings (such as labels and explanations) were written as:

Serial.print(“Example debug message”);

Formatting these strings differently drastically reduced memory usage. The new format is as follows:

Serial.print(F(“Example debug message”));

Additionally, creating a flags structure for Boolean operators that act as flags in the code reduced memory usage. Originally, flags were individual Boolean variables, written as:

bool flag_1;

bool flag_2;

These operators could be rewritten in a structure as:

struct Flags {

bool flag_1 : 1;

bool flag_2 : 1;};

Flags flags;

To call a flag from this structure, such as flag_1, you would write flags.flag_1.

## Soldered Protoboard

The soldered protoboard prototype was created to get feedback on the device before ordering custom PCBs. It was delivered to OTs in Kingston, Ontario, who tested it with clients and by themselves.

### Physical Component / Enclosure

The soldered protoboard prototype had a full 3D printed enclosure that resembled Concept 2. The enclosure was too large to fit on regular 3D printer build plates, so it was printed in quarters, and assembled after printing. The fully assembled prototype can be seen below.

Figure 21: Soldered breadboard prototype of the Chatterbox.

The two parts of the top and bottom halves of the enclosure were connected using screws initially. To facilitate printing and to allow the screws to connect both parts, the screw posts were split at an angle, as shown in the cross-section below.

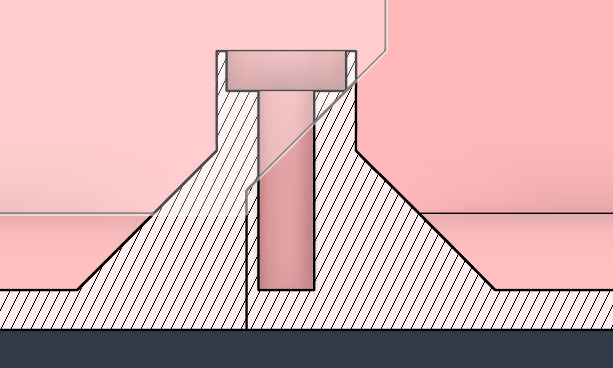
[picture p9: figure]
Cross-section of the screw posts, showing the angled split to facilitate printing.

Figure 22: Section view of the screw connection between quarters of the Chatterbox.

This method did not work as well as hoped. It was difficult to screw the parts together without introducing a noticeable gap, as can be seen on the top half of the enclosure. The connection was also not as strong as hoped and allowed for flexion and separation in the parts.

The front of the enclosure has two labeled ports for the assistive switches used for single or dual switch scanning. The four buttons on top of the device are for direct access to individual messages, and the toppers can be twisted on and off by hand. There are four holders for images that correspond to the messages on each button, and LEDs that light up for visual feedback. There are also holes on top for sound to enter and escape for the microphone and speaker, respectively.

Figure 23: Side view of the soldered protoboard prototype of the Chatterbox.

The side view of the enclosure shows the port for the USB to connect to the microcontroller, and the power and mode switches. The mode switch changes between recording and playback, and the power turns the device on and off. The USB port can be used to updated firmware, or power the device off the USB.

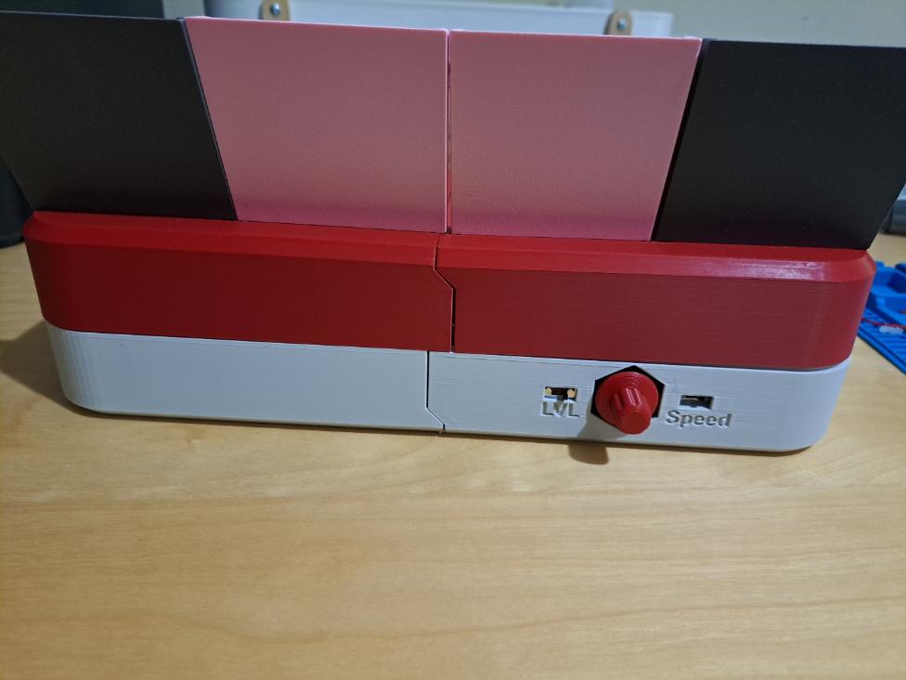
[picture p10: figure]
The back of the enclosure for the Chatterbox, showing the volume knob, and level and speed switches.

Figure 24: Back view of the soldered protoboard prototype of the Chatterbox.

The volume is adjusted at the back of the enclosure with the red knob, and the level and delay timing (Speed) are adjusted with the three-position switches on either side of the knob.

#### Button Bases

To make parts simpler to print and handle, and to make it easier to replace broken parts, the button bases that hold the tactile switches for direct message access were designed to be printed separately from the enclosure. The bases connect to the enclosure with snap fits. The snap fits are based on the ideas from Slant 3D[^1]. These snap fits were used throughout the design to connect parts without the need of other fasteners.

Figure 25: Section view of the direct access button parts.

The bases are also flat on one side to make printing easier, and give space for the wires from the tactile switches to clear the caps.

Figure 26: The button base of the direct access buttons.

#### Swappable button caps

The button caps were designed to be easily swappable without the need for tools. These are based on the Switched Adapted Toys 3D Printed Switch (https://www.switchedtoys.org/pages/3d-printed-switch-button). The button cap insert (yellow in the figure) has the threads to twist onto the base, and the cap (in teal) can slide freely up and down on the insert.

A change to their design was to stop the threads and have a smooth section of base the insert can slide and spin on. The intention of this section is to prevent over-tightening that could break the parts or cause a switch to be permanently pressed.

### Electrical Components

This prototype consisted mostly of the same electrical components as the solderless breadboard prototype, but had a few extra components, listed below.

Part | Quantity | Cost (CAD) | Link
9V battery clip | 1 | $0.59 | 232 Keystone Electronics | Battery Products | DigiKey (https://www.digikey.ca/en/products/detail/keystone-electronics/232/303804)
Mono jacks | 2 | $3.00 ($1.50 each) | MJ-3502 Same Sky (Formerly CUI Devices) | Connectors, Interconnects | DigiKey (https://www.digikey.ca/en/products/detail/same-sky-formerly-cui-devices/MJ-3502/281321)
General purpose protoboard | 1 | $7.02 | 12070 SparkFun Electronics | Prototyping, Fabrication Products | DigiKey (https://www.digikey.ca/en/products/detail/sparkfun-electronics/12070/5230951)
40x60mm protoboard | 1 | $2.50 | 4785 Adafruit Industries LLC | Prototyping, Fabrication Products | DigiKey (https://www.digikey.ca/en/products/detail/adafruit-industries-llc/4785/13617529)

### Code Structure / Function

The code developed on the solderless breadboard was added to this prototype, with one major change: rather than using a three-position switch to move between ON-OFF-RECORD, the ON-OFF is controlled by a single two-position switch, and the mode is controlled by another. The mode is controlled by the voltage reading from a resistor ladder attached to the Mode switch.

## Printed Circuit Board (PCB) Prototype

The PCB prototype is essentially the same as the soldered protoboard prototype. There are minor changes to the position of switches and jacks, but the main difference is the use of custom PCBs to make assembly easier.

Figure 27: The completed Chatterbox with assistive switches.

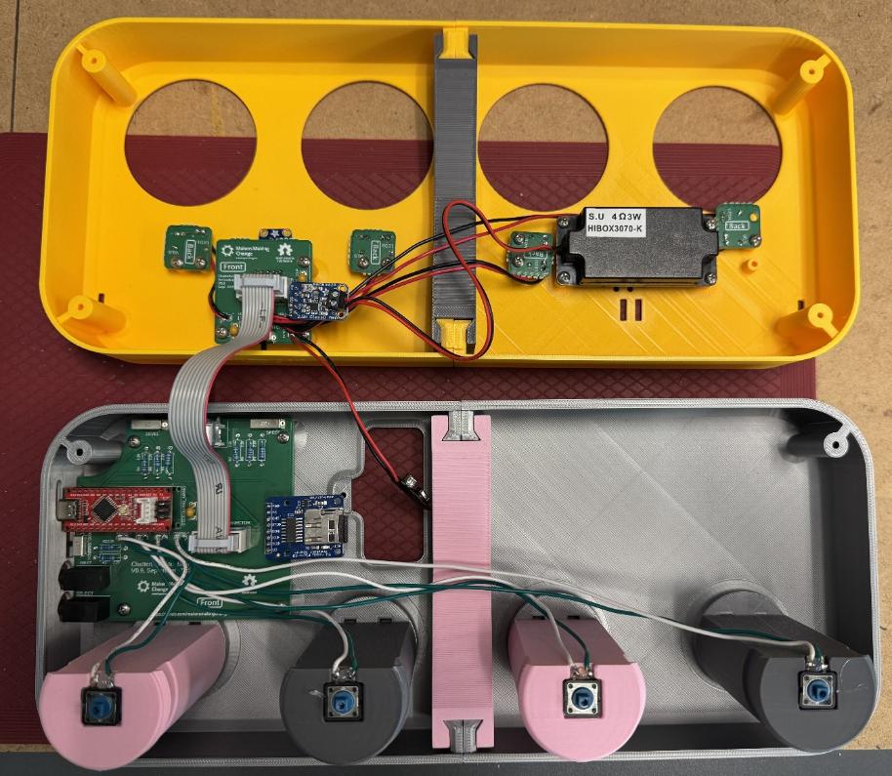
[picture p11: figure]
View of the inside of the Chatterbox, showing the electronics in the top and bottom halves.

Figure 28: Internal components of the PCB prototype of the Chatterbox.

### Physical Components / Enclosure

Most of the physical components received only minor changes, such as the location of the switches and switch ports; however, some parts had major changes.

#### Connecting top and bottom quarters to each other

The top and bottom quarters are connected to each other using a snap fit, like those in the button bases, and another 3D printed part to add rigidity (the centre support).

Figure 29: Section view of the snap connection between the quarters of the Chatterbox enclosure.

The snap fits were sized so that the top quarters cannot snap together with the bottom quarters. The different sizes prevent mistakes while assembling the enclosure.

The centre support slides over a dovetail and holds the quarters of the top and bottom halves together more firmly than with the snap fits alone. The support also adds strength and rigidity across the centre of the enclosure, which was lacking in the soldered breadboard prototype.

Figure 30: View of the centre supports holding the bottom enclosure quarters together.

#### Battery Cover

A battery cover design from the Open Playback Recorder was added to more securely hold the 9V battery, and to make it easier to replace the battery if it dies.

Figure 31: Initial design of the battery cover.

### Electronic Components

The major change the to the electronic components was to add the custom PCBs. Due to size limits from most PCB manufacturers, the board was split into two designs: the Main PCB, and the Secondary PCB. The Secondary PCB also had breakaway smaller PCBs for each of the LEDs.

The schematics for all PCBs can be found in the Detailed Design section.

#### Main PCB

The Main PCB was named so because it is the larger board with more of the electrical components. The Main PCB is mounted to the bottom half of the enclosure, with the switches and volume knob sticking out the side to be accessible.

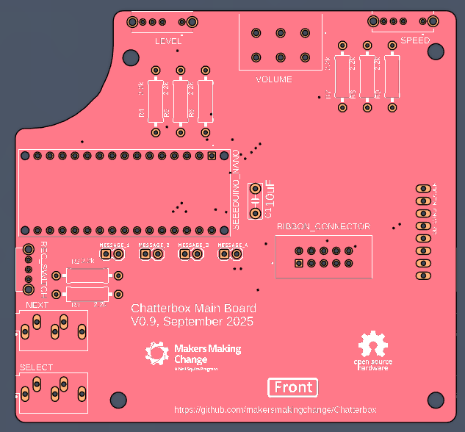
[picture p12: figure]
Top view of the Main PCB.

Figure 32: Front (left) and back (right) views of the main PCB.

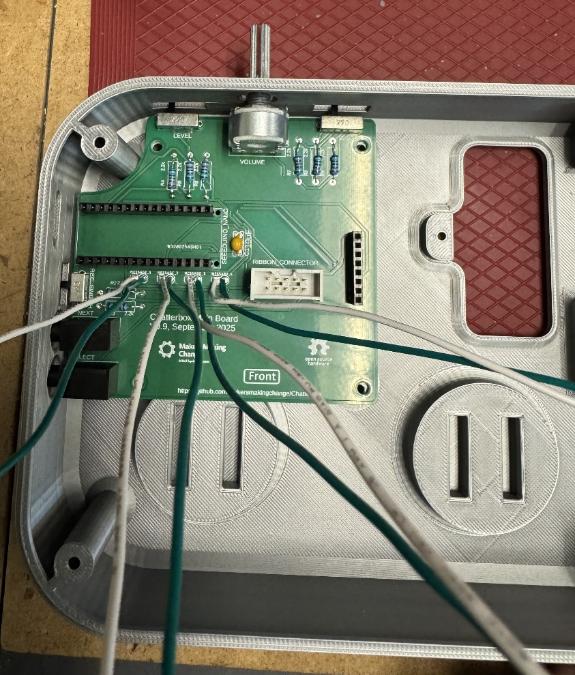
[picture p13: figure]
Main PCB mounted in the bottom half of the enclosure, without the microcontroller or SD card reader attached.

Figure 33: Main PCB inserted into enclosure bottom.

#### Secondary PCB

The Secondary PCB was named so as it is the smaller of the two boards and does not have the microcontroller. It was originally designed to be made with the four LED boards as part of it, connected by mouse bites which could be broken off by the maker. The goal of this PCB panelization was to reduce cost and complexity of the build.

Figure 34: Front (left) and back (right) of the secondary and LED PCBs.

#### LED PCBs

The LED PCBs were named so because they were made to more consistently connect and position the LEDs and their resistors. They were made to be broken off the Secondary PCB. The mouse bites were more difficult to break than expected, and they drastically increased the cost of ordering the PCBs. PCBWay treated the Secondary board as five PCB designs on one board, making them $75 to order.

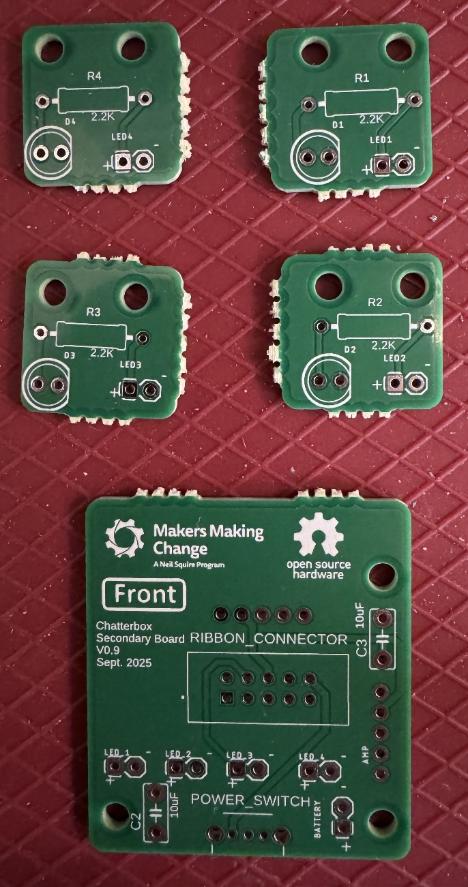
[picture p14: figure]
LED PCBs broken off from the Secondary PCB.

Figure 35: Secondary and LED PCBs after they have been broken apart.

## Prototype Decisions

Prototype | Decision (Abandon, Modify, Proceed) | Justification
Solderless breadboard | Modify | Created to easily test code and hardware, but not useful for a final device.
Soldered Protoboard | Modify | The increased cost and design work to create PCBs is warranted by the complexity of assembling the soldered protoboard version.
PCB Prototype | Modify | The panelized PCB for the LEDs and Secondary board were much more expensive than ordering them separately, so needed to be separated.

# Detailed Design

## Overview

The Chatterbox is a switch scanning communication device which provides auditory feedback to guide the user while scanning.

The Chatterbox has been certified by the Open Source Hardware Association (OSHWA) (https://certification.oshwa.org) with OSHWA UID CA000070 (https://certification.oshwa.org/ca000070.html).

Figure 36: The completed Chatterbox with assistive switches.

Some key information is highlighted in the table below.

Table 1: Key Information

Key Information of the Chatterbox
Cost | $135.00 (CAD)
Dimensions (mm) | 330 x 140 x 65 (main enclosure body only) 330 x 156 x 135 (including label holders and volume knob)
Mass (g) | 835
Number of 3D printed parts | 32 (13 unique parts)
Mass of 3D printed parts (g) | 658
Print Time | 19 hours, 12 minutes
Assembly Time | 1.5 hours

The Chatterbox is divided into the following systems:

- Enclosure
- Direct access buttons
- Electrical components
- Firmware

Each subsystem and the key design decisions are summarized in this section.

### Enclosure

The enclosure can be further broken down into its own subsystems:

- Enclosure body
- Centre supports
- Label Holders
- Battery cover
- Volume knob

#### Enclosure Body

The enclosure body was split into four parts so that the Chatterbox could be printed on most commercially available FDM printers. The 330 mm length is too long to fit in a standard printer workspace, which is typically around 250x250x250 mm. The bottom quarters and top quarters connect to each other by a snap fit to reduce the number of required screws and make assembly/disassembly easier. The snap fit is based on those shown in a video by Slant 3D[^2]. (https://www.youtube.com/watch?v=RTQjvYENR7w) The top quarters are incompatible with the bottom quarters, so a maker cannot connect the wrong parts together.

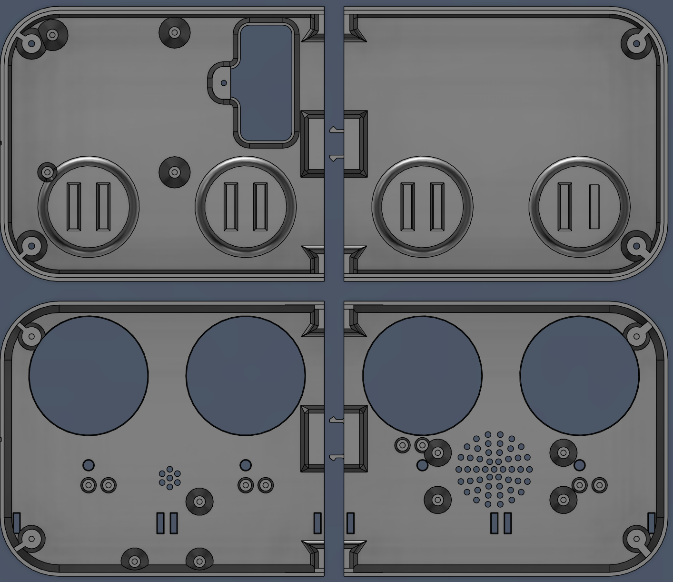
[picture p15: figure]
Screenshot of the inside of the four quarters of Chatterbox.

Figure 37: View of the inside of the top and bottom halves of the enclosure.

Figure 38: View of the outside of the top and bottom of the enclosure.

All ports and access points on the sides and back of the enclosure are labelled with their respective functions. Slide switches have labelling to show what each position does (ex: Record vs Playback mode, Off vs On). Due to size and positioning constraints of the PCB, some of the labelling is somewhat cluttered on the side of the enclosure.

Figure 39: Screenshot of the labels on the side of the Chatterbox.

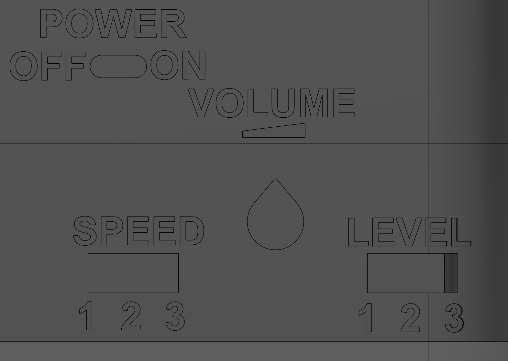
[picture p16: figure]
Screenshot showing the labeling on the back of the Chatterbox.

Figure 40: Screenshot of the labels on the back of the Chatterbox.

The snap fit between the two bottom quarters is dimensioned in the following figure:

Figure 41: Dimensions of the snap fit connections between the bottom quarters of the Chatterbox.

The snap connection between the top quarters is dimensioned below:

Figure 42: Dimensions of the snap fit between the top quarters of the Chatterbox.

Fillets and chamfers were added to break sharp edges on the snap fits.

#### Centre Supports

The centre supports were created to add more strength to the enclosure. These supports make the connection between quarters more snug, and add rigidity down the centre of the enclosure body. The added rigidity helps reduce twisting, bending, and flexing of the enclosure. The centre support for the bottom and top halves is the same, so there is only one STL file to print it.

The centre supports were again designed without the need for hardware to secure them, to reduce cost and increase ease of assembly/disassembly. The supports slide onto a dovetail joint to lock the two quarters together, and hold the support in place. Once the top and bottom halves are together, the two centre supports rest on each other, securing them vertically so they cannot move in the enclosure.

Figure 43: Screenshot of the bottom centre support holding the two bottom quarters together.

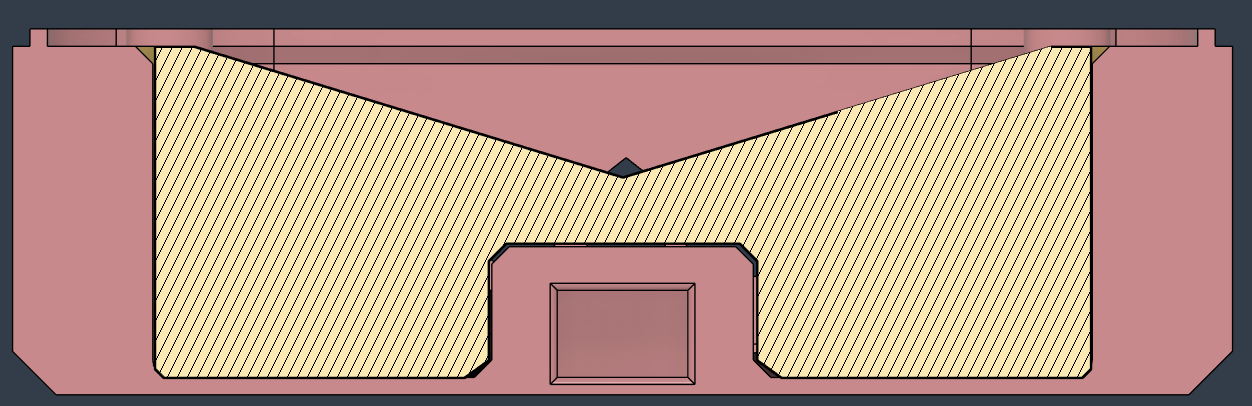
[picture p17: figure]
Cross-section view of the centre support showing how it sits on the two quarters.

Figure 44: Cross-sectional view of the bottom centre support.

Figure 45: Cross-sectional view of both centre supports.

#### Label Holders

The label holders position the paper labels users can print out to identify the different messages on the Chatterbox. The label holders snap into the top of the enclosure with a similar snap fit used to connect the enclosure quarters. The label holders can hold a 76x72 mm label (wider than it is tall). The requestors of the device asked for the holders to fit labels of that size.

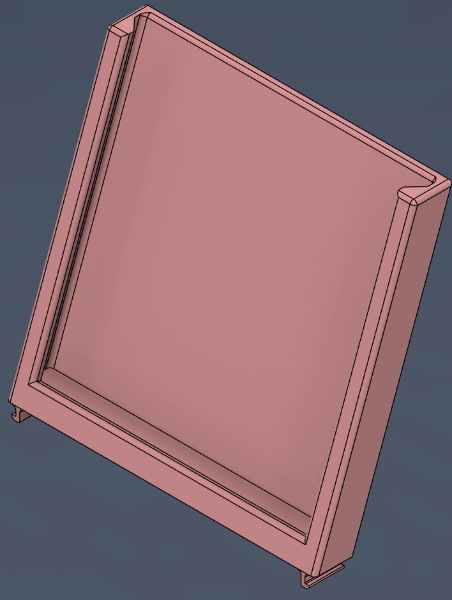
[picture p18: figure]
Screenshot of a label holder.

Figure 46: Label holder.

The snap fit tabs for connecting the label holders to the enclosure are 36.6 mm from the centre line of the holders to the inside, flat edge (without the hook). The dimensions for those tabs are below.

Figure 47: Dimensions of the snap fit tabs for the label holders.

#### Battery Cover

The battery cover holds the battery in place inside the Chatterbox, and makes it easy to access/replace the battery. The cover was adapted from a previous version of the Open Playback Recorder.

Figure 48: Screenshot of the battery cover.

The cutout at the back makes it easier to push a battery in and out of the cover. The battery cover is screwed into the bottom enclosure. The screw ensures a secure fit for the battery, and the need for a tool to remove the battery reduces the chances someone will accidentally access the battery or other internal components.

#### Volume knob

The volume knob slips over the exposed end of the potentiometer that controls the volume of the Chatterbox. The volume knob was reused from the Open Playback Recorder.

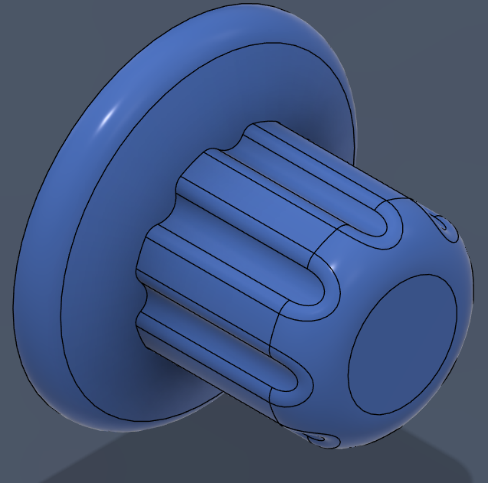
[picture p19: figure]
Screenshot of the volume knob.

Figure 49: Screenshot of the 3D printed volume knob that covers the potentiometer.

### Direct Access Buttons

The direct access buttons are used to directly access messages on the Chatterbox, both for recording and playback. The buttons can be broken into the following subsystems:

- Button base (orange)
- Button insert (green)
- Button cap (turquoise)

Figure 50: Screenshots of the direct access button assembly. Left: an exploded view of the base, insert, and cap. Right: Assembled view showing the base inserted into the enclosure bottom.

The direct access buttons were split into these subsystems to make 3D printing easier, and allow users to switch out the button caps without using tools. The idea behind switching the caps without tools is to allow users to customize switch caps for different messages, and easily change the cap based on the message. The base, insert, and cap are based on a design by Switched Adapted Toys (https://www.switchedtoys.org/products/switch-kit-diy-3d-printed-switch-button-assembly-kit). The insert snaps into the cap, and then screws onto the base. The cap can slide up and down on the insert, letting it rest on a switch and activate the switch when pressed.

#### Button Base

Figure 51: Screenshot of the button base, showing the flat surface for 3D printing.

The button base is flat on one side to have a large surface for printing, and to give clearance to the wires that go to the switch. The switch sits in the cutout on the top of the base and is glued in place. The threads on the base are short, and the narrow section lets the insert spin freely. This flat section was added to prevent over-tightening the cap and insert. Over-tightening could damage the parts and/or constantly activate the switch.

The threads on the button base and insert are ISO Metric profile M45x4.5. That thread profile was suggested by Fusion 360 when modelling the threads, and was found to work effectively during test printing. The threads on the base were pressed in by 0.3 mm to add clearance for different printing tolerances.

The snap fit on the bottom of the button base is the same design as between the enclosure quarters. Dimensions are below. The sketch on the left is for the hole in the bottom enclosure quarters the button base snaps into, and the right side shows the dimensions of the snap tabs on the button base.

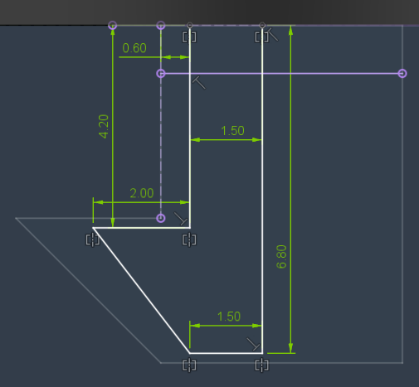
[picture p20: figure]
Dimensions of the snap fit tabs that are on the button base with the outline of the slot visible.

Figure 52: Dimensions of the slots and tabs for the button base snap fit. Left: Dimensions of the slot in the bottom enclosure. Right: Dimensions of the tabs on the button base, with the outline of the slots also visible.

#### Button Insert

Figure 53: Screenshot of the button insert.

The button insert has four tabs which can flex to snap fit into the button cap. The threads on the inside of the insert allow users to screw the button insert and cap onto the button base. The dimensions for the insert tabs, cutouts, and inner and outer diameters are shown below.

Figure 54: Dimensions of the button insert. The inner and outer diameters are shown, as well as the snap tabs and cutouts which allow the tabs to flex.

The insert is 10 mm tall, the tabs are 3 mm tall, and the cutouts to allow the tabs to flex are 5 mm deep.

#### Button Cap

The button cap has four slots which the flexible parts of the insert snap into. These slots also allow the cap to slide up and down on the insert to activate the switch. The cap was designed to print either on the flat top, or from the bottom up with bridging. The cap was designed to be printed with bridging to give more flexibility in custom 3D printed top options.

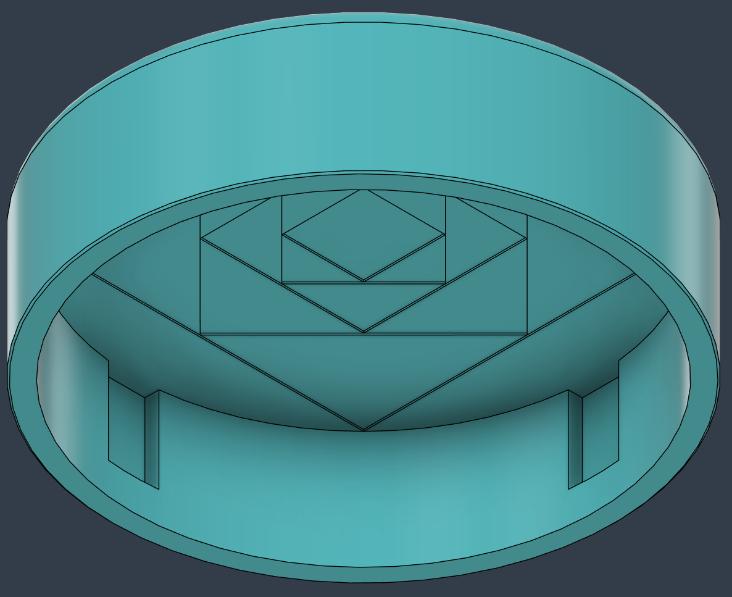
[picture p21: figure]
Screenshot of the underside of the button cap.

Figure 55: Screenshot of the underside of the button cap showing the slots for the snap fit tabs, and the design to reduce bridging distances.

Figure 56: Cross-section of the button cap.

The dimensions of the cap are shown below.

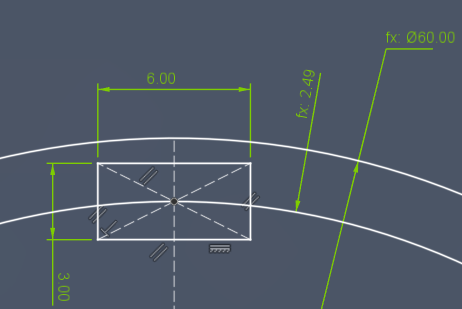
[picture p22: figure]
Dimensions of the button cap.

Figure 57: Dimensions of the button cap. The outer diameter, thickness, and the size of the slot for the snap fit tab are shown.

The button cap is 17.5 mm tall, and the slots for the tabs on the insert are 11.25 mm tall, from the bottom inside surface of the cap. The cap has the same thickness all around.

### Electrical Components

The electrical components can be split into two subsystems:

- Off-the-shelf electronics
- Custom PCBs
  - Main PCB
  - Secondary PCB
  - LED PCBs

#### Off-the-shelf components

The off-the-shelf components were mostly inherited from the Open Playback Recorder design, and kept because they worked effectively for recording and playing back messages. The Bill of Materials (BOM) has links to all the parts, prices, and quantities.

Part Name | Description/Use | Rationale for Choice
Seeeduino Nano | Microcontroller | - Had enough pins for required functions - Worked with TMRpcm library for recording and playing messages - Cheaper than Arduino Nano
Audio Amplifier (Pam8302) | Audio amplifier | - Gave flexibility in the speaker choice and placement compared to built-in amp/speaker combos
Mono speaker (4Ω 3W) | Speaker | - Small enough to easily fit, but strong enough to be heard easily in various environments
Audio potentiometer | Volume control | - Intuitive volume control
Micro SD Reader | Reading and writing to a micro SD card | - Gave flexibility in the messages that could be stored and positioning compared to not using an SD card
Micro SD card | Storing recorded messages | - Gave flexibility in the length and number of messages that could be recorded
Microphone (MAX9814) | Recording audio | - Small footprint microphone
Switches (B3F-5050) | Direct access switches | - Commonly used switch in many MMC devices - Reduces costs and complexity for MMC as we can order these in large quantities and use across many devices
Slide Switch (SPST) | Power and mode switches | - Affordable option used in multiple MMC devices
3.5 mm Mono Jack | Assistive switch ports | - Affordable mono jack option used in multiple MMC devices
LEDs | Visual indicators for recording and playing back messages | - Affordable LEDs - Did not require LEDs to change colours, etc.
Resistors (2.2k Ω) | - Dropping voltage for LEDs - Resistor ladders for reading switch positions | - Drops voltage appropriately for LEDs - Drops voltage sufficiently to differentiate between switch positions - One value for all resistors to eliminate errors from incorrect resistor placement during assembly
Female headers (5, 8, and 15 pin) | Plugging in microcontroller, amp, microphone, and SD card reader to PCBs | - Used headers to make it easier to replace broken parts or salvage working boards from the Chatterbox
9V battery | Powering the Chatterbox | - Delivered sufficient power for the Chatterbox - Smaller footprint than using combinations of other batteries (AA, AAA, etc.)
Capacitors (10µF) | Steadying voltage on power and audio lines | - Sufficient value to steady power and audio line voltages - Reduces noise in signals
9V battery clip | Clip to attach 9V batteries to the PCB | - Easy to attach/detach the battery
10 pin ribbon cable | Connecting main and secondary PCBs together | - Enough pins to send required signals between the two boards - Reduces complexity of assembly than attaching wires independently
10 pin ribbon cable connector | Connect ribbon cable to PCBs | - Needed to connect ribbon cable to PCBs
Slide switch (SPDT) | Level and speed selection | - Simple and intuitive method for selecting levels and speeds
24 AWG wire | - Connecting LED PCBs to Secondary PCB - Connecting direct access switches to Main PCB | - Common wire size used for MMC devices - Sufficient for current being passed along the wires

#### Custom PCBs

To increase the reliability and durability of the PCBs, some of the default values in the Fusion 360 Design Rules were changed. Specifically, the width of the traces was changed, and this change was made across all PCBs.

Design Rule/Part | Description | Updated Value
Copper Width | Sets the default and minimum copper trace widths allowed on the PCB. | Minimum: 16 mil* Preferred: 24 mil
Power Trace Width | Manually updated the width of any trace which was carrying power or high current (9V power, 5V power, 3.3 V power). | 50 mil

*Note: the default unit of PCB rules is mil (thousandths of an inch). 1 mil = 0.0254 mm

Additionally, a ground pour was created on both sides of all boards (except the LED PCB, which was only done on one side since the board wiring is so simple). Ground planes were created across the entire top and bottom surfaces of the boards, making wiring simpler and grounds more reliable.

The ground pour was added to both sides of the boards, and then the Autorouter was used to run traces on the PCBs. The Autorouter routes were then manually inspected and modified to make sure there weren’t any isolated ground pours, and that copper traces were the correct width.

We used screws to mount all PCBs as we wanted these connections to be strong, reliable, and less likely to be affected by tolerance differences from different printers/materials.

##### Main PCB

The Main PCB did not change from the PCB Prototype. The schematic for the Main PCB is below.

Figure 58: Screenshot of the electronic schematic for the Main PCB.

The power capacitor ensures a clean, steady voltage is supplied from the battery to the microcontroller.

Figure 59: Picture of the front surface of the Main PCB.

The Main PCB is connected to the Secondary PCB by a 10-pin ribbon cable. The switches for each individual message are connected to the Main PCB by standard hookup wires (24 AWG). We recommend solid core wires because there is less chance of stray wire strands shorting components on the PCB.

##### Secondary PCB

We caught a mistake with some wiring on the Secondary PCB, and moved the LED PCBs to a separate board/schematic to decrease the cost of ordering them. The schematic and model of the Secondary PCB are below.

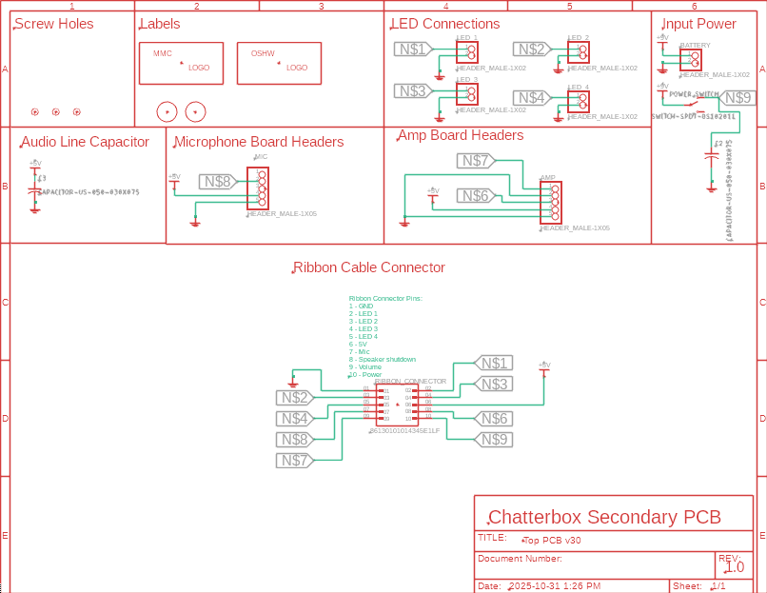
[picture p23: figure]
Screenshot of the schematic of the Secondary PCB.

Figure 60: Screenshot of the electronic schematic of the Secondary PCB.

The capacitor on the power line ensures a clean, steady power supply from the battery to the ribbon cable connector. The capacitor on the Audio Line ensures a clean, steady supply of power to the Microphone and Amp boards, as changes in voltage could affect the audio quality.

Figure 61: Screenshot of the front side of the Secondary PCB.

##### LED PCBs

The LED PCBs were moved to their own board, and makers are encouraged to order 20 of these boards since they need four per Chatterbox, and get five of each of the other boards anyway (enough for five Chatterboxes total). The schematic and model of the PCB are below.

Figure 62: Screenshot of the electronic schematic for the LED PCBs.

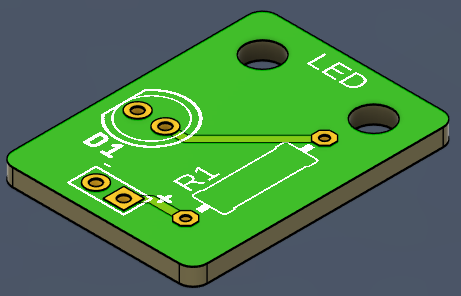
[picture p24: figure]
Screenshot of the 3D model of the LED PCB.

Figure 63: Screenshot of the front side of the LED PCB.

The LED PCBs are connected to the Secondary PCB using standard hookup wire (24 AWG). We again recommend solid core wire to reduce the chance of stray wires creating shorts on the PCB.

### Firmware

The code is the same as it was for the PCB Prototype. The firmware currently uses 70% of program storage space, and 72% of dynamic memory. Once the firmware reached a certain level of memory use (the exact value was not determined), the messages would not play back (they were treated as empty). Future updates to the code will need to consider these memory restrictions, unless a new microcontroller is used. The firmware can be found in the GitHub. The flowcharts showing the general code structure are below.

#### General Code Structure

Figure 64: Flowchart showing the general code structure of the Chatterbox firmware.

#### Playback Code Structure

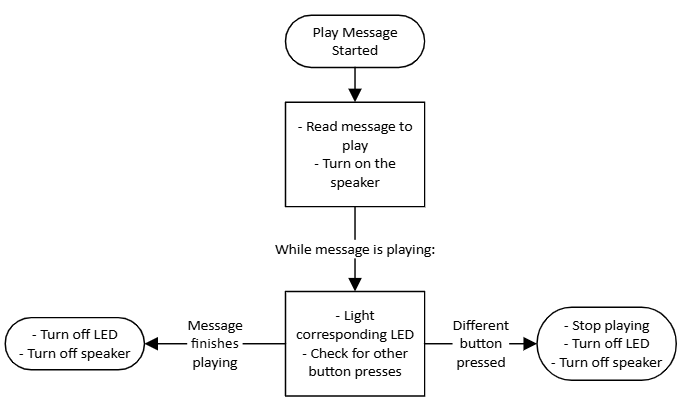
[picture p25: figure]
Flowchart showing the structure of how a message is played back.

Figure 65: Flowchart showing how a message is played back.

#### Recording Code Structure

Figure 66: Flowchart showing how the Chatterbox responds to inputs when in the record mode.

#### Arduino Libraries

The following Arduino libraries are used in the Chatterbox. The purpose of each library is included in the table.

Library | Author | Purpose
TMRpcm (https://github.com/TMRh20/TMRpcm) | TMRh20 | Handles recording and playback of messages.
SD | Arduino | Handles interactions with the SD card.
SPI | Arduino | Handles communication with serial peripheral interface (SPI) devices.
StateMachine (https://github.com/jrullan/StateMachine) | jrullan | Allows for simple implementation of a state machine.
neotimer (https://github.com/jrullan/neotimer) | jrullan | Allows for integrated timing with the state machine library.

#### Input Handling

##### Switch Debounce

Switch debouncing is handled in software. When a switch is pressed, there is a 50 ms delay in the code to “pause” it. The 50 ms delay was chosen based on testing with previous devices, and was found to be long enough to debounce effectively, without being noticeable to a user.

##### User-controlled settings

The settings that are controllable by a user without changing the firmware were all identified by the original requestors of the device. These include:

- Volume
- Playback delay
- Level
- Mode

The volume is controlled with a logarithmic potentiometer to match general analogue volume control on other devices (turning a knob adjusts the volume). The maximum volume is controlled in the firmware.

The playback delay has three durations that are set in the firmware. The user can select between these three options using a three-position slide switch. The choice of having three discrete options, and the default durations (2, 4, and 6 seconds) were made by the original requestors. The slide switch was chosen as it would only require on input pin on the microcontroller to change the delay, and provided feedback to the user on which delay was selected.

The level is also selected by using a slide switch. The level had to be adjustable by a secondary user without having to interact with the firmware. The slide switch was chosen for the same reason as for the playback delay.

The mode had to be controlled by the user to let them switch between recording and playing back messages. Having the distinct modes prevents users from accidentally deleting messages when trying to play them back. Modes are controlled with a two-position slide switch. The slide switch for changing modes was chosen for the same reason it was chosen for playback delay.

##### Firmware-controlled settings

Most values and settings in the firmware should not be changed. Most of the variables are set for the custom PCBs, or to control the firmware. Do not change the firmware unless you make corresponding changes to the PCBs, wiring of the device, and controls within the firmware.

There are a few settings that a user might want to adjust which are controlled in the firmware. These settings were kept to firmware as they weren’t settings a user would need to adjust often, if at all. The settings we identified were:

- Default playback delay values
- Blink interval
- Record interval
- Maximum volume

These variables are separated out in the code to make it easy to find them, and reduce the chance of accidentally changing the wrong variable. Currently they are between lines 112 and 118 of the firmware. They are sandwiched between two lines of commented percent signs (%%%%%%%) to make them easy to find when scrolling through the firmware.

The default playback delay values are an array with three values, and are in milliseconds (ms). The delay values can be set to any millisecond duration and should go from shortest to longest duration in the array.

The blink interval is the time for which LEDs are lit and off when blinking. The default of 500 ms was chosen arbitrarily as a medium blinking speed. The value can be changed to any millisecond value (shorter will speed up the blinking, longer will slow it down). Before changing, note that a longer blink interval might result in dead space at the beginning of a recorded message, as users might not realize the message has started recording as quickly as when the interval is smaller.

The record interval is how long a user needs to hold down a button in record mode before the firmware deletes the existing message and starts recording a new one. The one second value was chosen as a long enough time that someone likely won’t accidentally start recording, but short enough that it won’t be frustrating. The value can be changed to any duration, and is in ms.

The maximum volume is controlled as part of the TMRpcm library. It can be 0 to 7, and 5 was found to be a good value. Setting the maximum too high resulted in the speaker not playing, and too low will make it so users can’t hear the messages.

# Verification and Validation

This section defines the verification and validation (V&V) activities required to confirm that the device meets its design requirements, user and stakeholder needs, and applicable safety and performance expectations.

- Verification ensures the design was built correctly according to specifications.
- Validation ensures the right design was built, meeting user needs in real-world use.

## Verification

### Verification Objective

Confirm that all design requirements have been met through objective evidence such as inspection, analysis, or testing.

### Verification Methods

Common verification methods include:

- Inspection: Visual or measurement confirmation (e.g., enclosure dimensions, solder joints).
- Analysis: Analytical confirmation (e.g., thermal calculations, firmware memory usage).
- Test: Functional testing under controlled conditions (e.g., switch response time).
- Demonstration: Simple operational proof (e.g., assembly demonstration).

### Verification Matrix

Note: all verification was completed by Stephan Dobri (SD) as part of the design process of the Chatterbox.

Requirement ID | Requirement | Verification ID | Verification Method | Acceptance Criteria | Result / Status (Pass/fail, comment?) | Evidence Reference (linking to results/data that showed we passed the requirement)
F01 | Secondary users must be able to record their own messages. | V01 | Demonstration | The device allows users to record their own messages without needing to remove the SD card or using external firmware (ex: using a computer). | Pass | SD
F02 | Messages up to a minute in length must be possible to record. | V02 | Demonstration | Messages from <1 second to 60 seconds can be recorded. | Pass | SD recorded a message that was 78 seconds long and played it back successfully.
F03 | The device must record at least three separate messages. | V03 | Demonstration | The Chatterbox can record at least three messages. | Pass | SD
F04 | The device must work with single switch scanning. | V04 | Demonstration | The Chatterbox can be used with single switch scanning through an external assistive switch. | Pass | SD
F05a | Users must be able to add labels or pictures to help identify the messages | V05a | Demonstration | User can make and add their own labels to the messages. | Pass | SD
F05b | Labels must be a minimum size of 76x76 mm. | V05b | Inspection | Labels are 76x76 mm. | Marginal Labels are 71x71 mm. Larger labels cannot be accommodated without making the device larger than the maximum length (F09). | Requestors stated slightly smaller labels than originally asked were large enough.
F06 | The delay between messages while switch scanning can be modified. | V06 | Demonstration | Secondary users can change the delay between messages while switch scanning without changing the firmware. | Pass | SD
F07 | The volume must be adjustable by secondary user. | V07 | Demonstration | Secondary users can adjust the volume while using the Chatterbox without changing the firmware. | Pass | SD
F08 | The device must be able to be cleaned with a damp cloth. | V08 | Demonstration | The Chatterbox can be cleaned with a damp cloth. | Pass | SD
F09 | The device must fit on a student’s lap tray (maximum length 330 mm). | V09 | Inspection | Maximum length less than 330 mm | Pass | SD
F10 | The device must be able to record and play at least two different levels of messages. | V10 | Demonstration | The Chatterbox can switch between and use at least two levels of messages without adjusting firmware. | Pass | SD
F10a | The device must have means to change level. | V10a | Demonstration | Secondary users can change the levels without changing the firmware. | Pass | SD
F10b | The device must have an indicator of current level. | V10b | Visual inspection | Secondary users can tell which level the Chatterbox is on without listening to messages. | Pass | SD
F11 | Integrated buttons on the device must be parallel to the surface the device is mounted or placed upon. | V11 | Inspection | The surface of the integrated buttons is parallel to the surface the Chatterbox is mounted/placed upon. | Pass | SD
F12 | The device enables switch-enabled auditory scanning. | V12 | Demonstration | The Chatterbox can be used with single switch scanning through an external assistive switch. | Pass | SD
F12a | The device plays pre-recorded messages when triggered by primary user. | V12a | Demonstration | The Chatterbox can be used with single switch scanning through an external assistive switch. | Pass | SD
F12b | The device must be able to record a message for each position. | V12b | Demonstration | The device allows users to record their own messages on each button independently, without needing to remove the SD card or using external firmware (ex: using a computer). | Pass | SD
F12c | The device must have a visual indicator for each position. | V12c | Visual Inspection | There are visual indicators to identify each message position. | Pass | SD
F12d | The device must have a means for indicating the current position. | V12d | Visual Inspection | Users can identify which message is being played, recorded, or selected from visual inspection. | Pass | SD
F12e | The device must play a selected message again when selected by the user. | V12e | Demonstration | The primary user can select a message to play back while switch scanning and the Chatterbox will play the full selected message. | Pass | SD
F13 | The device must have a way to indicate which position is being recorded. | V13 | Visual Inspection | Users can identify which message is being played, recorded, or selected from visual inspection. | Pass | SD
N/A | The device is more affordable than commercially available options. | V14 | Inspection | The device costs less than $300 CAD | Pass | Commercially Available Options section; SD
N/A | Determine the expected battery life of the device. | V15 | Inspection | The expected battery life is measured and reported. | Run times: On in either mode: 19 hours Playing a message at full volume: 3.2 hours Recording a message: 18 hours See appendix for details on measuring durrent draw. | SD
N/A | The device can survive being dropped off a desk/lap tray | V16 | Demonstration | Parts do not break when dropped off a desk. | Bottom of the enclosure split along layer lines after multiple drops. All other parts survived. See appendix for details on drop tests. | SD, MMC staff
N/A | The device can be printed on different 3D printers and with different filament types. | V17 | Demonstration | The parts print successfully, and the tolerances work on multiple different printers and with different filaments. | Pass | SD

### Verification Summary

All requirements were met except F05. Recommend that original requirement is amended for smaller size (71 mm instead of 76 mm). This reduction should be validated with the stakeholders to ensure that this smaller size still meets their needs (i.e., not concerned about compatibility with existing larger templates).

## Validation

### Validation Objective

Confirm that the final design meets user and stakeholder needs in its intended context of use.

### Validation Questions

The following list of questions was used for brainstorming what to ask the users on the Microsoft Form.

- LEDs
  - Bright enough?
  - Easy to see for primary and secondary user?
  - Colour preference?
  - Do they need to stick out of the top?
- Label holders
  - Ease of creating new labels
  - Ease of swapping labels
  - Visibility of labels
  - Is the 76 mm size critical? Are there existing templates / labels that require this size?
- User Guide
  - Clarity of information
  - Length appropriate?
  - Anything missing?
- Recording
  - Easy to record new messages?
- Playback
  - Playback clear/any audio issues?
  - Sound board option?
- Switch Scanning
  - Works as intended?
  - Any issues with any assistive switches?
  - Are default delay times sufficient?
  - Switch scanning delay from start or end of message?
  - Using single switch scanning vs dual switch scanning
    - Need separate operating modes? (delay triggers playback instead of advancing message)
- Slide switches
  - Easy to access and move switches?
  - Easy to control position/know what speed or level you’re in?
- Switch caps
  - Easy to customize?
  - Easy to switch out caps?
- Size and shape
  - Is height of device acceptable?
  - Weight appropriate?
- Any other comments/feedback?

### Validation Matrix

Validation ID | Validation Objective | Participant(s) | Procedure | Acceptance Criteria | Result / Comment

End-user Validation
Val01 | Ensure audio playback is clear and audible. | Surrey School AAC Team, Kingston OTs, Set BC team | Provide prototype for participants to test. | Testers verify the audio is clear and audible. | Testers felt the audio quality was lower than they’d like.
Val02 | Ensure secondary users can record messages. | Surrey School AAC Team, Kingston OTs, Set BC team | Provide prototype for participants to test. | Secondary users recorded their own messages without issue. | Pass
Val03 | Ensure single switch scanning works as intended. | Surrey School AAC Team, Kingston OTs, Set BC team | Provide prototype for participants to test. | Users navigated messages through single switch scanning. | Pass
Val04 | Ensure dual switch scanning works as intended. | Surrey School AAC Team, Kingston OTs, Set BC team | Provide prototype for participants to test. | Users navigated messages with dual switch scanning. | Pass
Val05 | Determine appropriate default delay time lengths between messages. | Surrey School AAC Team, Kingston OTs, Set BC team | Provide prototype for participants to test. | Testing participants provide appropriate default delay times. | Pass
Val06 | Determine if changing switch caps is difficult for secondary users. | Surrey School AAC Team, Kingston OTs, Set BC team | Provide prototype for participants to test. | Secondary users can change the switch caps without separating the top and bottom halves of the enclosure. | Pass
Val07 | Ensure the device is an acceptable size. | Surrey School AAC Team, Kingston OTs, Set BC team | Provide prototype for participants to test. | Testers verify the Chatterbox is an acceptable size. | Pass
Val08 | Ensure the device is an acceptable weight. | Surrey School AAC Team, Kingston OTs, Set BC team | Provide prototype for participants to test. | Testers verify the Chatterbox is an acceptable weight. | Pass
Val09 | Ensure switching between modes is reliable. | Surrey School AAC Team, Kingston OTs, Set BC team | Provide prototype for participants to test. | Secondary users can reliably change between recording and playback modes. | Testers felt the original slide switches were hard to access (did not protrude enough from the enclosure)
Val10 | Ensure switching between levels is reliable. | Surrey School AAC Team, Kingston OTs, Set BC team | Provide prototype for participants to test. | Secondary users can reliably select the level they would like using the slide switch. | Same feedback as Val09.
Val11 | Ensure visual feedback for the level is clear. | Surrey School AAC Team, Kingston OTs, Set BC team | Provide prototype for participants to test. | Secondary users can tell which level the Chatterbox is on by looking at the slide switch. | Pass
Val12 | Ensure switching between delays is reliable. | Surrey School AAC Team, Kingston OTs, Set BC team | Provide prototype for participants to test. | Secondary users can reliably select the delay they would like using the slide switch. | Same feedback as Val09.
Val13 | Ensure visual feedback for the delay is clear. | Surrey School AAC Team, Kingston OTs, Set BC team | Provide prototype for participants to test. | Secondary users can tell which delay the Chatterbox is on by looking at the slide switch. | Pass
Val14 | Ensure visual feedback for which message is playing, recording, or being selected is clear. | Surrey School AAC Team, Kingston OTs, Set BC team | Provide prototype for participants to test. | Users can see and differentiate between the indicator LEDs. | Testers requested the LEDs protrude more from the top of the enclosure for increased visibility.
Val15 | Ensure the label holders are sufficiently large. | Surrey School AAC Team, Kingston OTs, Set BC team | Provide prototype for participants to test. | Users can see the labels. | Pass
Val16 | Ensure secondary users can create labels for messages. | Surrey School AAC Team, Kingston OTs, Set BC team | Provide prototype for participants to test. | Secondary users can create their own labels printed on paper. | Pass
Val17 | Ensure secondary users can change the labels for messages. | Surrey School AAC Team, Kingston OTs, Set BC team | Provide prototype for participants to test. | Secondary users do not report issues adding or removing paper labels. | Testers were concerned about durability of the label holders, but did not report any issues with them currently.
Val18 | Ensure device function is simple enough that users are learning to switch scan, not learning to use the device. | Surrey School AAC Team, Kingston OTs, Set BC team | Provide prototype for participants to test. | Users are able to learn switch scanning, rather than the specifics of how to use the Chatterbox. | Testers did not report on this metric.
Val19 | Ensure the User Guide is not missing information. | Surrey School AAC Team, Kingston OTs, Set BC team | Provide participants with the User Guide to read through and reference when testing the Chatterbox. | Secondary users provide feedback on what information should be added to the User Guide. | Pass: testers did not recommend any new information be added to the User Guide.
Val20 | Ensure the User Guide is written clearly. | Surrey School AAC Team, Kingston OTs, Set BC team | Provide participants with the User Guide to read through and reference when testing the Chatterbox. | Secondary users provide feedback on how to make the User Guide more clear. | One tester suggested changing from a labelled picture of the Chatterbox to a wireframe diagram to make it easier to read (especially if printed in black and white).

Volunteer Maker Validation
Val21 | Ensure Maker Guide is not missing information. | Volunteer maker in Burnaby, BC | Have volunteer maker go through Maker Guide. | Volunteer provides feedback on missing information that can be added. | Volunteer suggested minor revisions/additions.
Val22 | Ensure Maker Guide is written clearly. | Volunteer maker in Burnaby, BC | Have volunteer maker go through Maker Guide. | Volunteer provides feedback to improve clarity that can be completed. | Volunteer suggested minor revisions/additions.
Val23 | Ensure maker can follow Assembly Guide to create a functioning device. | Volunteer maker in Burnaby, BC | Have volunteer maker make a prototype. | Volunteer successfully builds a working Chatterbox. | Volunteer successfully built working Chatterbox.

#### Validation Methods

##### User Testing

User testing was completed by multiple user groups, and all groups were given access to a Microsoft Form to collect feedback (https://forms.office.com/Pages/DesignPageV2.aspx?origin=NeoPortalPage&subpage=design). The questions in the form were designed to help guide user testing, to collect specific feedback we identified as required, and to allow open feedback. The users were also provided the User and Quickstart Guides to learn how to use the Chatterbox.

##### Maker Testing

A volunteer maker in Burnaby, BC, was asked to assemble a Chatterbox, following the Assembly Instructions in the Maker Guide. The goal was to have someone unfamiliar with the device follow the instructions to make sure they are clear and nothing is missing.

### Validation Summary

#### User Testing

Forms feedback summary:

- Audio quality isn’t great
- Volume should be louder
- Hard to access slide switches
  - Might want to add in the slide switch cap things, or make them stick out further from the enclosure
- Switch caps were an issue
  - Hard to change
  - Rocked and sometimes lead to not activating properly
  - Sliding against hole made unpleasant sound (which was also audible in recordings)
- Would like space for tactile labels in front of the buttons
- Label holders come off easily
- Some users thought it was big and bulky
  - Height was the main concern
- Battery cover can fall into enclosure when changing the battery
- A handle might make it more portable
- The buttons sometimes got caught on the enclosure and stayed pressed
- Some users might want to mount the device, so mounting options might be useful

Need to clarify the use case of this device: Not a full-on communication device meant for everyday use and communication, but as a training device. Need to make it clear it has limited functionality compared to things like tablet communication devices.

##### Suggested Changes

The suggested changes from user feedback are listed below, with the corrections made to address the suggestions highlighted.

- Reduce height as much as possible
  - Height reduced by 15 mm, and cannot be reduced further without rearranging PCBs
- Make LEDs poke out of top a bit more
  - Height of posts for the screws on the LED PCBs was reduced to allow LEDs to stick out of the top of the enclosure further (1.5 mm more than initially)
- Reduce wobble on switches
  - Wobble reduced, but not eliminated, by changing clearance on parts that connect
  - Sound of wobble reduced by increasing the diameter of the holes in the top of the enclosure (less interaction between button caps and enclosure)
- Make switches more responsive to activation from different angles.
  - Diameter of holes in the top of the enclosure increased to reduce button caps getting caught on enclosure/allowing more options for activation when pressing on different parts of the cap
  - Button base height increased to reduce interactions between the button caps and enclosure top
- Add covers for slide switches to make them easier to move
  - Created covers for the slide switches to make them easier to access and move
- Increase size of lip around the battery holder to keep it from falling into the enclosure when changing the battery
  - Lip size increased to stop battery holder falling into the enclosure, while maintaining printability

The following suggested changes were not addressed, and the reason for not addressing them is highlighted below each suggestion:

- Improve audio quality
  - This is a limitation of the hardware, and would require a full rework of the device
- Increase volume
  - This is also a limitation of the hardware, and would require a full rework of the device
- Place tactile label holders in front of the buttons
  - Moving the label holders to directly in front of the switches would greatly increase the size of the Chatterbox
  - Smaller tactile labels on the chamfer or front face of the Chatterbox are something that could be considered for future improvements
- Adding a handle to make it more portable
  - While a handle would make it more portable, the general use case would not be for someone to carry it in their hands regularly
  - The height was reduced which may help with the portability (this feedback came before the height was decreased)
- Adding mounting options to the device
  - We did not receive enough information to accurately design mounting options based on the suggestion
  - The flat bottom of the Chatterbox makes Velcro mounting options easy to add
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

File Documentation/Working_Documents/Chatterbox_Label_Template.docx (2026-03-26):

© 2025 by Neil Squire. This work is licensed under the CC BY SA 4.0 License: http://creativecommons.org/licenses/by-sa/4.0 Files available at makersmakingchange/Chatterbox: A switch scanning AAC device for users with visual impairment. Page 2 of 3

V1.0| December 2025 Chatterbox Label Template

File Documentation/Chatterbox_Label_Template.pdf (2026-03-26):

V1.0| December 2025

# Chatterbox Label Template

© 2025 by Neil Squire. (https://neilsquire.ca/)
This work is licensed under the CC BY SA 4.0 License: http://creativecommons.org/licenses/by-sa/4.0
Files available at makersmakingchange/Chatterbox: A switch scanning AAC device for users with visual impairment. (https://github.com/makersmakingchange/Chatterbox) | Page 1 of 2

V1.0| December 2025

# Chatterbox Label Template

© 2025 by Neil Squire. (https://neilsquire.ca/)
This work is licensed under the CC BY SA 4.0 License: http://creativecommons.org/licenses/by-sa/4.0
Files available at makersmakingchange/Chatterbox: A switch scanning AAC device for users with visual impairment. (https://github.com/makersmakingchange/Chatterbox) | Page 2 of 2

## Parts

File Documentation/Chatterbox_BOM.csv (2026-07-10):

Device: | Chatterbox
Version: | V1.0.0
Last Updated: | 2025-09-26
 |  |  |  |  |  |  |  | Total filament (g) |  | Unit Cost | Total Estimated Cost | Build Cost
 |  |  |  |  |  |  |  | 391 |  | $134.32 | $167.33
ID | Commercial Parts |  |  |  |  |  |  |  |  | $109.87 | $110.88
 | Part | Description | Model | Manufacturer | Supplier | QTY / Device | QTY / PKG | PKGs | $/ PKG | $ / Device | Total Estimated Cost |  | Link
 | Micro Controller (Seeeduino Nano) |  |  | Seeed Technology, Ltd. | Digikey | 1 | 1 | 1 | $11.07 | $11.07 | $11.07 |  | https://www.digikey.ca/en/products/detail/seeed-technology-co-ltd/102010268/10290292
 | Audio Amplifier (Pam8302) |  |  | Adafruit Industries LLC | Digikey | 1 | 1 | 1 | $6.13 | $6.13 | $6.13 |  | https://www.digikey.ca/en/products/detail/adafruit-industries-llc/2130/5761279
 | Mono Speaker (4Ω 3W ) |  |  | Adafruit Industries LLC | Digikey | 1 | 1 | 1 | $6.13 | $6.13 | $6.13 |  | https://www.digikey.ca/en/products/detail/adafruit-industries-llc/3351/6612456
 | Audio Potentiometer |  |  | Same Sky (Formerly CUI Devices) | Digikey | 1 | 1 | 1 | $2.65 | $2.65 | $2.65 |  | https://www.digikey.ca/en/products/detail/cui-devices/PTN16-A10125K1A2/20380750
 | Micro SD Reader |  |  | Adafruit Industries LLC | Digikey | 1 | 1 | 1 | $10.93 | $10.93 | $10.93 |  | https://www.digikey.ca/en/products/detail/adafruit-industries-llc/254/5761230
 | Micro SD Card |  |  | Adafruit Industries LLC | Digikey | 1 | 1 | 1 | $7.69 | $7.69 | $7.69 |  | https://www.digikey.ca/en/products/detail/adafruit-industries-llc/5252/15841478
 | Microphone (MAX9814) |  |  | Adafruit Industries LLC | Digikey | 1 | 1 | 1 | $12.35 | $12.35 | $12.35 |  | https://www.digikey.ca/en/products/detail/adafruit-industries-llc/1713/4990777
 | Buttons (B3F-5050) |  |  | Omron Electronics Inc-EMC Div | Digikey | 4 | 1 | 4 | $0.57 | $2.28 | $2.28 |  | https://www.digikey.ca/en/products/detail/omron-electronics-inc-emc-div/B3F-5050/368377
 | Slide switch (SPST) |  |  | C&K | Digikey | 2 | 1 | 2 | $0.95 | $1.90 | $1.90 |  | https://www.digikey.ca/en/products/detail/c-k/os102011ma1qn1/1981430
 | 3.5 mm Mono Jack |  |  | Same Sky (Formerly CUI Devices) | Digikey | 2 | 1 | 2 | $2.17 | $4.34 | $4.34 |  | https://www.digikey.ca/en/products/detail/cui-devices/SJ1-3535NG/738699
 | Blue LED |  |  | Wurth Elektronik | Digikey | 4 | 1 | 4 | $0.37 | $1.48 | $1.48 |  | https://www.digikey.ca/en/products/detail/w%C3%BCrth-elektronik/151051BS04000/4490009
 | Resistor (2.2k Ω) |  |  | Stackpole Electronics Inc | Digikey | 12 | 1 | 12 | $0.16 | $1.92 | $1.92 |  | https://www.digikey.ca/en/products/detail/stackpole-electronics-inc/CF18JT2K20/1741619
 | 5 pin female header |  |  | Sullins Connector Solutions | Digikey | 2 | 1 | 2 | $0.55 | $1.10 | $1.10 |  | https://www.digikey.ca/en/products/detail/sullins-connector-solutions/PPTC051LFBN-RC/807239
 | 15 pin female header |  |  | Sullins Connector Solutions | Digikey | 2 | 1 | 2 | $1.19 | $2.38 | $2.38 |  | https://www.digikey.ca/en/products/detail/sullins-connector-solutions/PPTC151LFBN-RC/810153
 | Battery, 9V |  |  | Duracell Industrial Corporation, Inc. | Digikey | 1 | 1 | 1 | $7.49 | $7.49 | $7.49 |  | https://www.digikey.ca/en/products/detail/duracell-industrial-operations-inc/9V/21259959
 | Capacitor, 10 uF |  | FG24X7R1A106KRT06 | TDK Corporation | Digikey | 3 | 1 | 3 | $0.50 | $1.50 | $1.50 |  | https://www.digikey.ca/en/products/detail/tdk-corporation/FG24X7R1A106KRT06/5802984
 | 9V Battery Clip |  |  | Keystone Electronics | Digikey | 1 | 1 | 1 | $0.86 | $0.86 | $0.86 |  | https://www.digikey.ca/en/products/detail/keystone-electronics/232/303804
 | #4 Sheet Metal Screw | #4 x 3/8" pan head, Phillips drive |  | Serpac | Digikey | 20 | 1 | 20 | $0.61 | $12.20 | $12.20 |  | https://www.digikey.ca/en/products/detail/serpac/6005/307599
 | Ribbon Cable |  |  | Assmann WSW Components | Digikey | 1 | 1 | 1 | $1.63 | $1.63 | $1.63 |  | https://www.digikey.ca/en/products/detail/assmann-wsw-components/H3DDS-1006G/1218627
 | Ribbon Cable Header |  |  | Amphenol ICC (FCI) | Digikey | 2 | 1 | 2 | $0.79 | $1.58 | $1.58 |  | https://www.digikey.ca/en/products/detail/amphenol-cs-fci/86130101014345E1LF/7592367
 | Slide switch (SPDT) |  |  | C&K | Digikey | 2 | 1 | 2 | $1.21 | $2.42 | $2.42 |  | https://www.digikey.ca/en/products/detail/c-k/os103011ma7qp1c/10063872
 | 24 gauge wire | May be useful to buy two colours |  | TE Connectivity Raychem Cable Protection | Digikey | 9 | 10 | 1 | $10.11 | $9.10 | $10.11 |  | https://www.digikey.ca/en/products/detail/te-connectivity-raychem-cable-protection/55A0111-24-9/2399803
 | 8 pin female header |  |  | Sullins Connector Solutions | Digikey | 1 | 1 | 1 | $0.74 | $0.74 | $0.74 |  | https://www.digikey.ca/en/products/detail/sullins-connector-solutions/PPTC081LFBN-RC/810147
 | Custom PCB |  |  |  |  |  |  |  |  | $8.00 | $40.00
 | Part | Description |  | Manufacturer | Supplier | QTY / Device | QTY / PKG | PKGs | $/ PKG | $ / Device | Total Estimated Cost |  | Link
 | Main PCB | Main PCB board |  |  |  | 1 | 5 | 1 | $5.00 | $1.00 | $5.00
 | Secondary PCB | Secondary PCB board |  |  |  | 1 | 5 | 1 | $5.00 | $1.00 | $5.00
 | LED PCB | Boards for LEDs |  |  |  | 4 | 20 | 1 | $5.00 | $1.00 | $5.00
 |  | Shipping |  |  |  | 1 | 5 | 1 | $25.00 | $5.00 | $25.00
 | 3D Printed Parts |  |  |  |  |  |  | 658 |  | $16.45 | $16.45
 | Part | Description | Filament Type | Filament | Color | QTY / Device | Mass (g) / Part | Total Mass | $ / kg | $ / Device | Total Estimated Cost |  | Link
 | Enclosure Bottom - Left |  | PLA |  | Any | 1 | 97 | 97 | $25.00 | $2.43 | $2.43 |  | 2h44m
 | Enclosure Bottom - Right |  | PLA |  | Any | 1 | 100 | 100 | $25.00 | $2.50 | $2.50 |  | 2h29m
 | Enclosure Top - Left |  | PLA |  | Any | 1 | 76 | 76 | $25.00 | $1.90 | $1.90 |  | 2h14m
 | Enclosure Top - Right |  | PLA |  | Any | 1 | 76 | 76 | $25.00 | $1.90 | $1.90 |  | 2h6m
 | Label Holder |  | PLA |  | Any | 4 | 19 | 76 | $25.00 | $1.90 | $1.90 |  | 31m (each)
 | Button Base |  | PLA |  | Any | 4 | 23 | 92 | $25.00 | $2.30 | $2.30 |  | 37m (each)
 | Button Cap |  | PLA |  | Any | 4 | 13 | 52 | $25.00 | $1.30 | $1.30 |  | 28m (each)
 | Button Insert |  | PLA |  | Any | 4 | 7 | 28 | $25.00 | $0.70 | $0.70 |  | 22m (each)
 | Centre Support |  | PLA |  | Any | 2 | 21 | 42 | $25.00 | $1.05 | $1.05 |  | 47m (each)
 | Slide Switch Cover |  | PLA |  | Any | 4 | 1 | 4 | $25.00 | $0.10 | $0.10 |  | 9m (each)
 | Slide Switch Cover Pin |  | PLA |  | Any | 4 | 1 | 4 | $25.00 | $0.10 | $0.10 |  | 7m (each)
 | Volume Knob |  | PLA |  | Any | 1 | 2 | 2 | $25.00 | $0.05 | $0.05 |  | 13m
 | Battery Cover |  | PLA |  | Any | 1 | 9 | 9 | $25.00 | $0.23 | $0.23 |  | 27m
 | Tools
 | Tool | Description |  | Manufacturer | Supplier |  |  |  |  |  |  |  | Link
 | Soldering Iron
 | 60Pb/40Tn Solder Wire
 | Needle Nose Pliers
 | Flush Cutters
 | Wire strippers
 | Desolder Pump (Optional)
 | Alternatives
 | Part | Description |  | Manufacturer | Supplier | QTY / Device | QTY / PKG | PKGs | $/ PKG | $ / Device | Total Estimated Cost |  | Link

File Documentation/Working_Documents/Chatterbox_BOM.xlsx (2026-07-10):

Device: | Chatterbox
Version: | V1.0.0
Last Updated: | 2025-09-26
 |  |  |  |  |  |  |  | Total filament (g) |  | Unit Cost | Total Estimated Cost | Build Cost
ID | Commercial Parts
 | Part | Description | Model | Manufacturer | Supplier | QTY / Device | QTY / PKG | PKGs | $/ PKG | $ / Device | Total Estimated Cost |  | Link
 | Micro Controller (Seeeduino Nano) |  |  | Seeed Technology, Ltd. | Digikey | 1 | 1 |  | $11.07 |  |  |  | https://www.digikey.ca/en/products/detail/seeed-technology-co-ltd/102010268/10290292
 | Audio Amplifier (Pam8302) |  |  | Adafruit Industries LLC | Digikey | 1 | 1 | 1 | $6.13 |  |  |  | https://www.digikey.ca/en/products/detail/adafruit-industries-llc/2130/5761279
 | Mono Speaker (4Ω 3W ) |  |  | Adafruit Industries LLC | Digikey | 1 | 1 | 1 | $6.13 |  |  |  | https://www.digikey.ca/en/products/detail/adafruit-industries-llc/3351/6612456
 | Audio Potentiometer |  |  | Same Sky (Formerly CUI Devices) | Digikey | 1 | 1 | 1 | $2.65 |  |  |  | https://www.digikey.ca/en/products/detail/cui-devices/PTN16-A10125K1A2/20380750
 | Micro SD Reader |  |  | Adafruit Industries LLC | Digikey | 1 | 1 | 1 | $10.93 |  |  |  | https://www.digikey.ca/en/products/detail/adafruit-industries-llc/254/5761230
 | Micro SD Card |  |  | Adafruit Industries LLC | Digikey | 1 | 1 | 1 | $7.69 |  |  |  | https://www.digikey.ca/en/products/detail/adafruit-industries-llc/5252/15841478
 | Microphone (MAX9814) |  |  | Adafruit Industries LLC | Digikey | 1 | 1 | 1 | $12.35 |  |  |  | https://www.digikey.ca/en/products/detail/adafruit-industries-llc/1713/4990777
 | Buttons (B3F-5050) |  |  | Omron Electronics Inc-EMC Div | Digikey | 4 | 1 | 4 | $0.57 |  |  |  | https://www.digikey.ca/en/products/detail/omron-electronics-inc-emc-div/B3F-5050/368377
 | Slide switch (SPST) |  |  | C&K | Digikey | 2 | 1 | 2 | $0.95 |  |  |  | https://www.digikey.ca/en/products/detail/c-k/os102011ma1qn1/1981430
 | 3.5 mm Mono Jack |  |  | Same Sky (Formerly CUI Devices) | Digikey | 2 | 1 | 2 | $2.17 |  |  |  | https://www.digikey.ca/en/products/detail/cui-devices/SJ1-3535NG/738699
 | Blue LED |  |  | Wurth Elektronik | Digikey | 4 | 1 | 4 | $0.37 |  |  |  | https://www.digikey.ca/en/products/detail/w%C3%BCrth-elektronik/151051BS04000/4490009
 | Resistor (2.2k Ω) |  |  | Stackpole Electronics Inc | Digikey | 12 | 1 | 12 | $0.16 |  |  |  | https://www.digikey.ca/en/products/detail/stackpole-electronics-inc/CF18JT2K20/1741619
 | 5 pin female header |  |  | Sullins Connector Solutions | Digikey | 2 | 1 | 2 | $0.55 |  |  |  | https://www.digikey.ca/en/products/detail/sullins-connector-solutions/PPTC051LFBN-RC/807239
 | 15 pin female header |  |  | Sullins Connector Solutions | Digikey | 2 | 1 | 2 | $1.19 |  |  |  | https://www.digikey.ca/en/products/detail/sullins-connector-solutions/PPTC151LFBN-RC/810153
 | Battery, 9V |  |  | Duracell Industrial Corporation, Inc. | Digikey | 1 | 1 | 1 | $7.49 |  |  |  | https://www.digikey.ca/en/products/detail/duracell-industrial-operations-inc/9V/21259959
 | Capacitor, 10 uF |  | FG24X7R1A106KRT06 | TDK Corporation | Digikey | 3 | 1 | 3 | $0.50 |  |  |  | https://www.digikey.ca/en/products/detail/tdk-corporation/FG24X7R1A106KRT06/5802984
 | 9V Battery Clip |  |  | Keystone Electronics | Digikey | 1 | 1 | 1 | $0.86 |  |  |  | https://www.digikey.ca/en/products/detail/keystone-electronics/232/303804
 | #4 Sheet Metal Screw | #4 x 3/8" pan head, Phillips drive |  | Serpac | Digikey | 20 | 1 | 20 | $0.61 |  |  |  | https://www.digikey.ca/en/products/detail/serpac/6005/307599
 | Ribbon Cable |  |  | Assmann WSW Components | Digikey | 1 | 1 | 1 | $1.63 |  |  |  | https://www.digikey.ca/en/products/detail/assmann-wsw-components/H3DDS-1006G/1218627
 | Ribbon Cable Header |  |  | Amphenol ICC (FCI) | Digikey | 2 | 1 | 2 | $0.79 |  |  |  | https://www.digikey.ca/en/products/detail/amphenol-cs-fci/86130101014345E1LF/7592367
 | Slide switch (SPDT) |  |  | C&K | Digikey | 2 | 1 | 2 | $1.21 |  |  |  | https://www.digikey.ca/en/products/detail/c-k/os103011ma7qp1c/10063872
 | 24 gauge wire | May be useful to buy two colours |  | TE Connectivity Raychem Cable Protection | Digikey | 9 | 10 | 1 | $10.11 |  |  |  | https://www.digikey.ca/en/products/detail/te-connectivity-raychem-cable-protection/55A0111-24-9/2399803
 | 8 pin female header |  |  | Sullins Connector Solutions | Digikey | 1 | 1 | 1 | $0.74 |  |  |  | https://www.digikey.ca/en/products/detail/sullins-connector-solutions/PPTC081LFBN-RC/810147
 | Custom PCB
 | Part | Description |  | Manufacturer | Supplier | QTY / Device | QTY / PKG | PKGs | $/ PKG | $ / Device | Total Estimated Cost |  | Link
 | Main PCB | Main PCB board |  |  |  | 1 | 5 |  | $5.00
 | Secondary PCB | Secondary PCB board |  |  |  | 1 | 5 | 1 | $5.00
 | LED PCB | Boards for LEDs |  |  |  | 4 | 20 | 1 | $5.00
 |  | Shipping |  |  |  | 1 | 5 |  | $25.00
 | 3D Printed Parts
 | Part | Description | Filament Type | Filament | Color | QTY / Device | Mass (g) / Part | Total Mass | $ / kg | $ / Device | Total Estimated Cost |  | Link
 | Enclosure Bottom - Left |  | PLA |  | Any | 1 | 97 |  | $25.00 |  |  |  | 2h44m
 | Enclosure Bottom - Right |  | PLA |  | Any | 1 | 100 |  | $25.00 |  |  |  | 2h29m
 | Enclosure Top - Left |  | PLA |  | Any | 1 | 76 |  | $25.00 |  |  |  | 2h14m
 | Enclosure Top - Right |  | PLA |  | Any | 1 | 76 |  | $25.00 |  |  |  | 2h6m
 | Label Holder |  | PLA |  | Any | 4 | 19 |  | $25.00 |  |  |  | 31m (each)
 | Button Base |  | PLA |  | Any | 4 | 23 |  | $25.00 |  |  |  | 37m (each)
 | Button Cap |  | PLA |  | Any | 4 | 13 |  | $25.00 |  |  |  | 28m (each)
 | Button Insert |  | PLA |  | Any | 4 | 7 |  | $25.00 |  |  |  | 22m (each)
 | Centre Support |  | PLA |  | Any | 2 | 21 |  | $25.00 |  |  |  | 47m (each)
 | Slide Switch Cover |  | PLA |  | Any | 4 | 1 |  | $25.00 |  |  |  | 9m (each)
 | Slide Switch Cover Pin |  | PLA |  | Any | 4 | 1 |  | $25.00 |  |  |  | 7m (each)
 | Volume Knob |  | PLA |  | Any | 1 | 2 |  | $25.00 |  |  |  | 13m
 | Battery Cover |  | PLA |  | Any | 1 | 9 |  | $25.00 |  |  |  | 27m
 | Tools
 | Tool | Description |  | Manufacturer | Supplier |  |  |  |  |  |  |  | Link
 | Soldering Iron
 | 60Pb/40Tn Solder Wire
 | Needle Nose Pliers
 | Flush Cutters
 | Wire strippers
 | Desolder Pump (Optional)
 | Alternatives
 | Part | Description |  | Manufacturer | Supplier | QTY / Device | QTY / PKG | PKGs | $/ PKG | $ / Device | Total Estimated Cost |  | Link

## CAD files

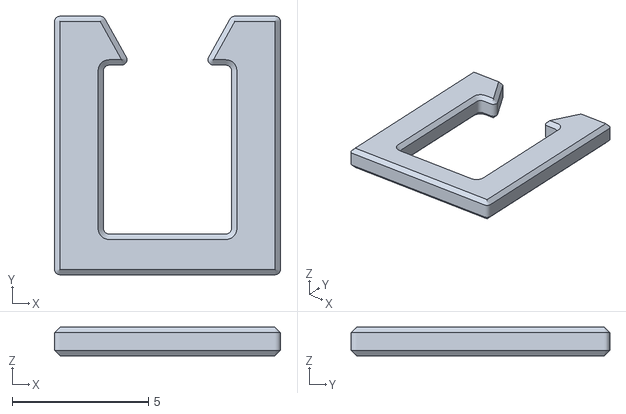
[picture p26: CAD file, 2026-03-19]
Build_Files/3D_Printing_Files/Slide_Switch_Cover_Pin.stl
8.30 x 9.50 x 1.05

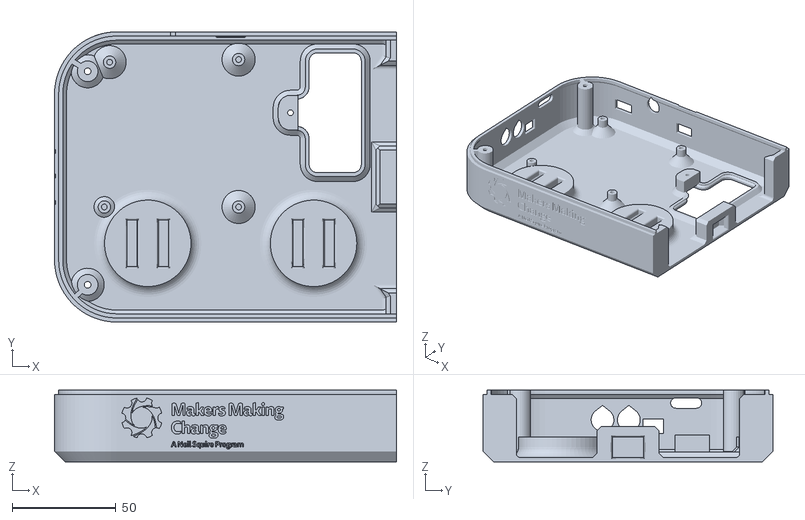
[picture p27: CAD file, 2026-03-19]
Build_Files/3D_Printing_Files/Enclosure_Bottom_Left.stl
165.0 x 140.0 x 34.5

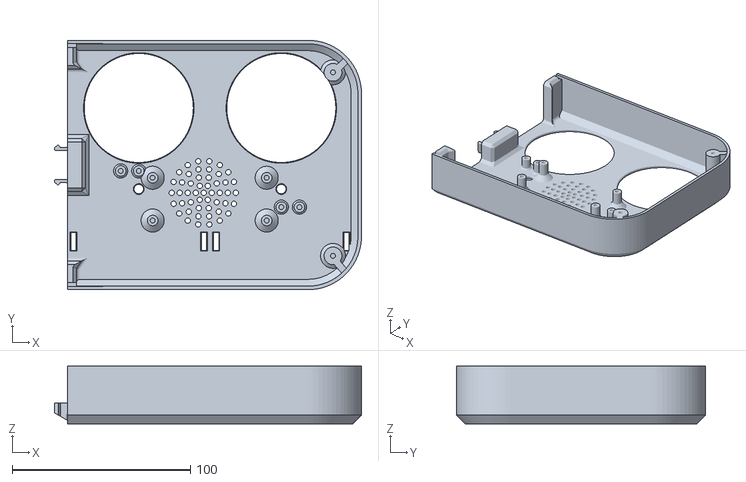
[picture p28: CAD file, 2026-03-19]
Build_Files/3D_Printing_Files/Enclosure_Top_Right.stl
172.3 x 140.0 x 32.5

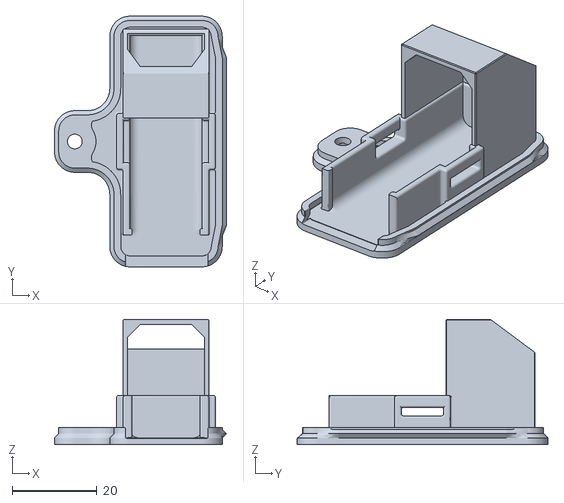
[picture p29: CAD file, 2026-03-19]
Build_Files/3D_Printing_Files/Battery_Cover.stl
40.7 x 59.3 x 29.6

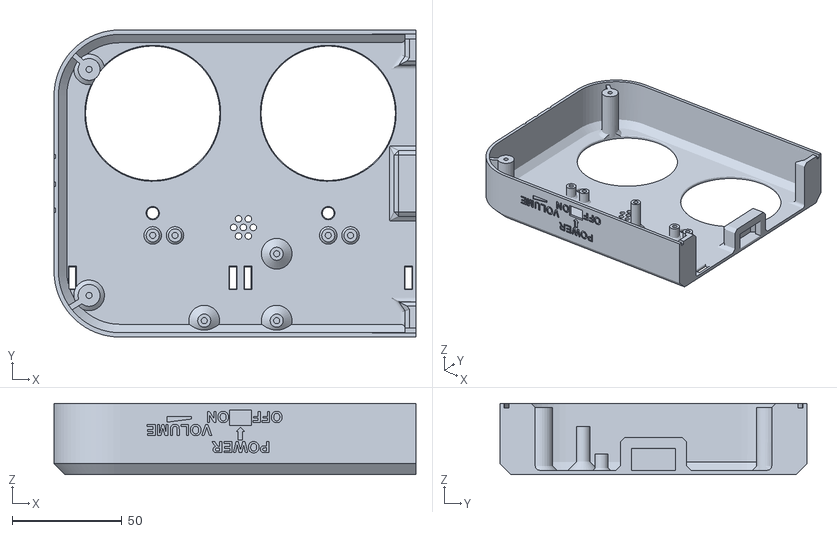
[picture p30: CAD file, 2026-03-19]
Build_Files/3D_Printing_Files/Enclosure_Top_Left.stl
165.0 x 140.0 x 32.5

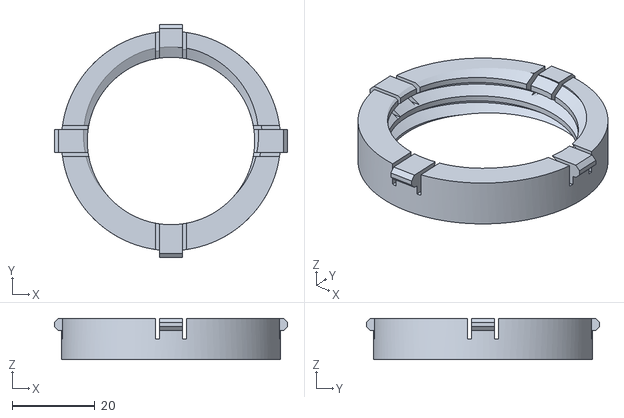
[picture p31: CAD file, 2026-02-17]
Build_Files/3D_Printing_Files/Button_Insert.stl
56.3 x 56.3 x 10.0

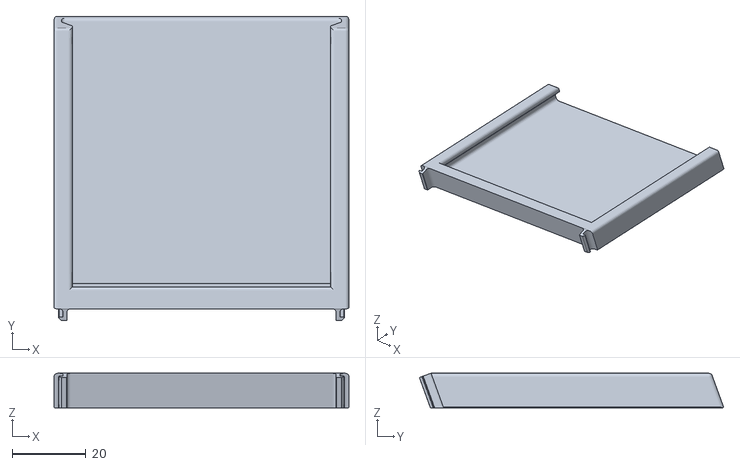
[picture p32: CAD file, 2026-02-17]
Build_Files/3D_Printing_Files/Label_Holder.stl
80.2 x 82.7 x 9.40

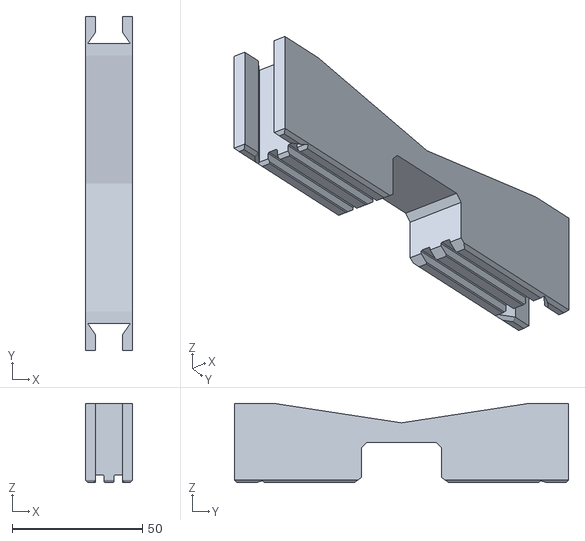
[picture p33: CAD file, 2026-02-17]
Build_Files/3D_Printing_Files/Centre_Support.stl
18.0 x 128.3 x 30.5

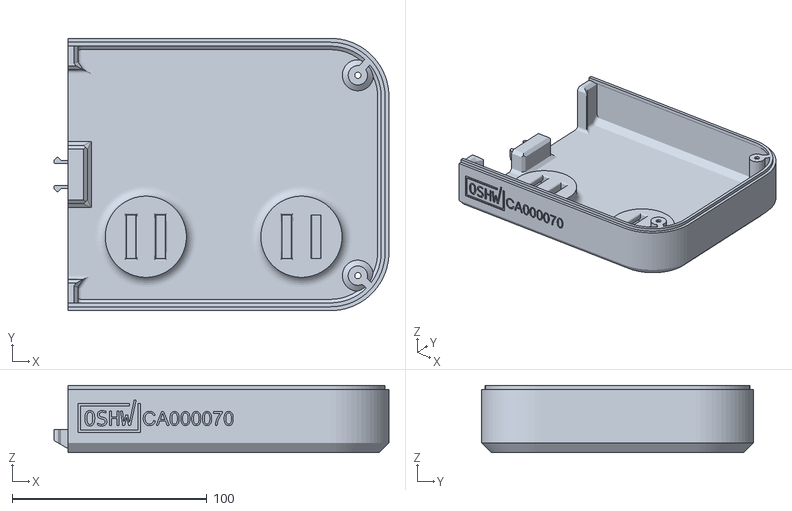
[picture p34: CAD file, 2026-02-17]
Build_Files/3D_Printing_Files/Enclosure_Bottom_Right.stl
172.2 x 140.0 x 34.5

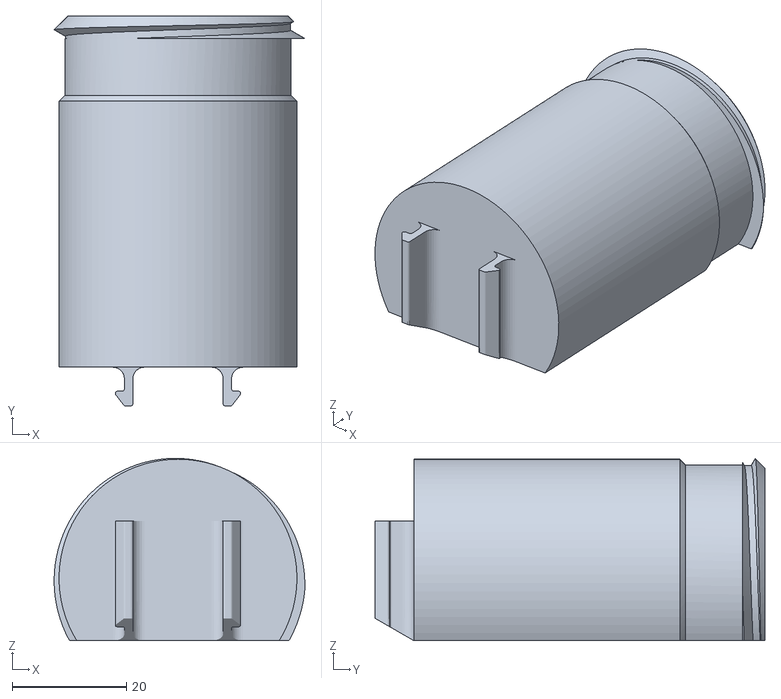
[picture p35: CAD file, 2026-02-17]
Build_Files/3D_Printing_Files/Button_Base.stl
44.0 x 68.4 x 32.0

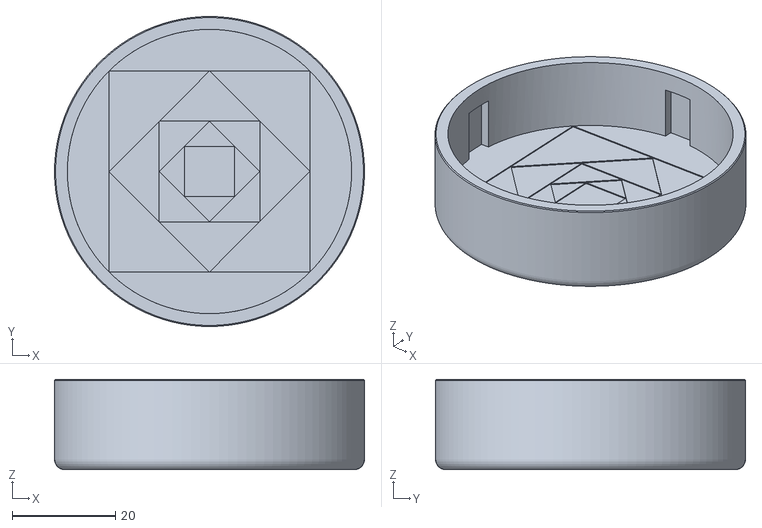
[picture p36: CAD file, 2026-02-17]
Build_Files/3D_Printing_Files/Button_Cap.stl
60.0 x 60.0 x 17.5

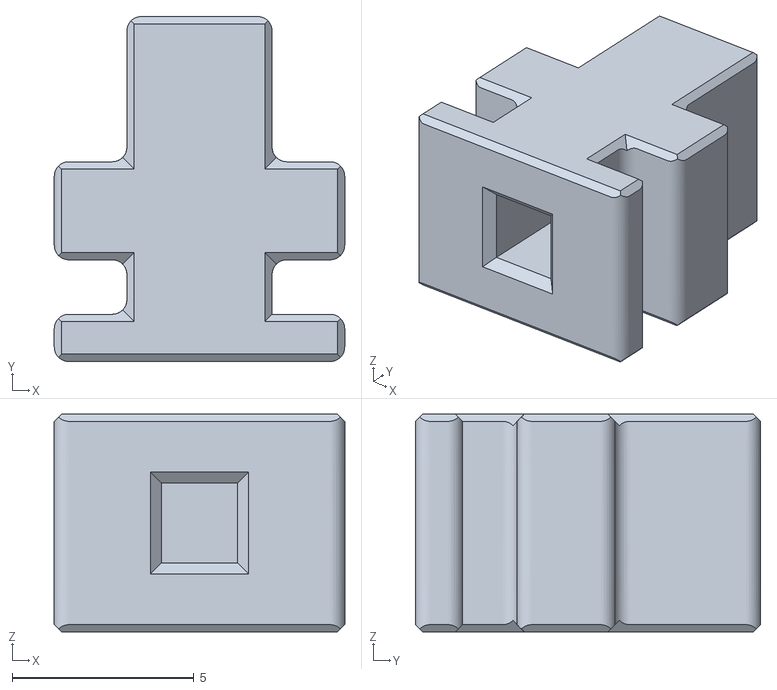
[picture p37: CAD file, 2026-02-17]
Build_Files/3D_Printing_Files/Slide_Switch_Cover.stl
8.00 x 9.50 x 6.00

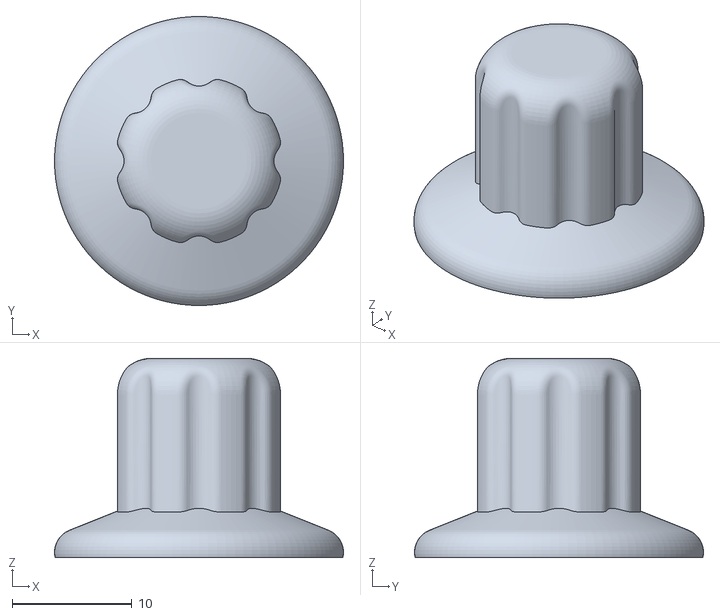
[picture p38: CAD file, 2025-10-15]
Build_Files/3D_Printing_Files/Volume_Knob.stl
24.1 x 24.1 x 16.6

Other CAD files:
Design_Files/CAD_Design_Files/PCB_Files/LED_PCB/LED_PCB.f3z
Design_Files/CAD_Design_Files/PCB_Files/Secondary_PCB/Secondary_PCB.f3z

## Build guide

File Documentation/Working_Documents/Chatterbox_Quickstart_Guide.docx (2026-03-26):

## Introduction

The Chatterbox is an Augmented and Alternative Communication (AAC) device that allows users to play pre-recorded messages using single or dual switch scanning. The Chatterbox provides auditory and visual feedback to indicate the message a user can play. The Chatterbox is meant for users with complex communication needs and visual impairment.

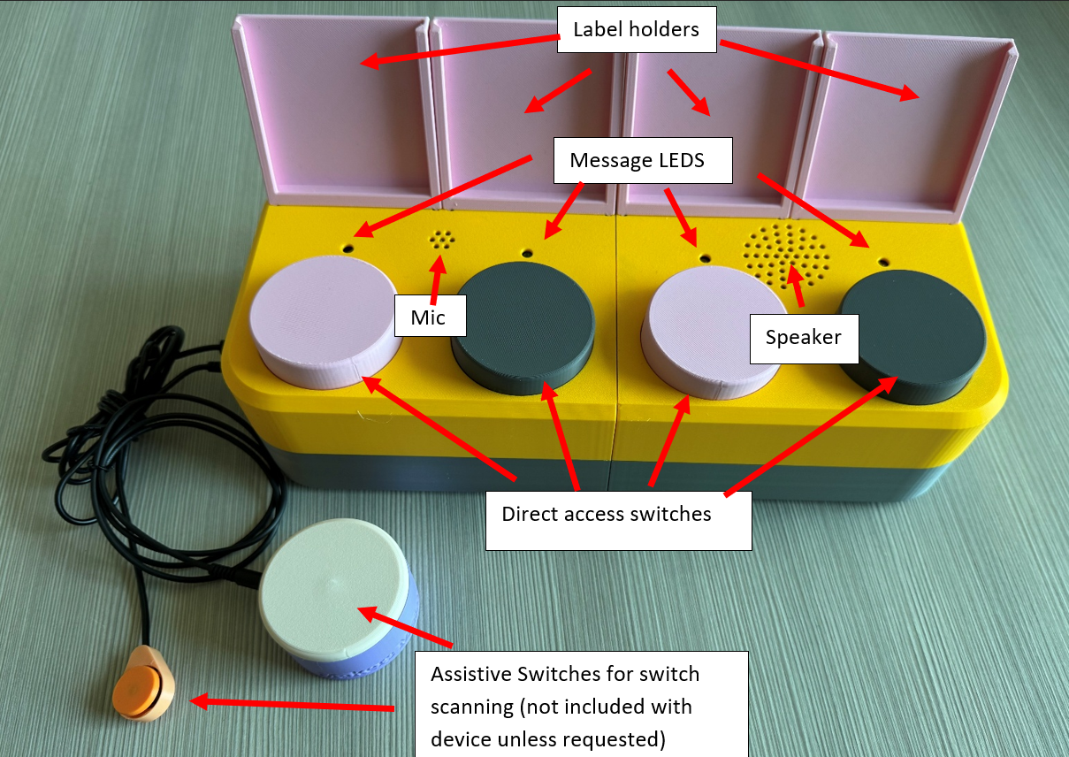
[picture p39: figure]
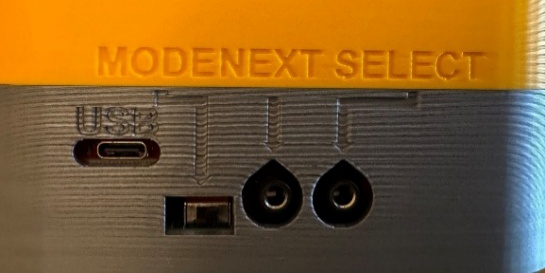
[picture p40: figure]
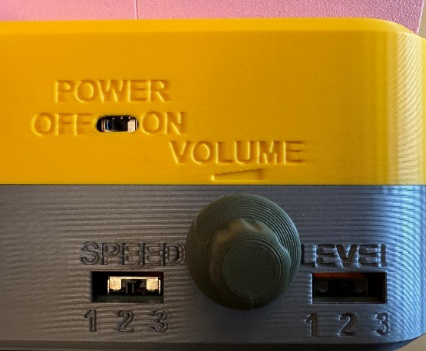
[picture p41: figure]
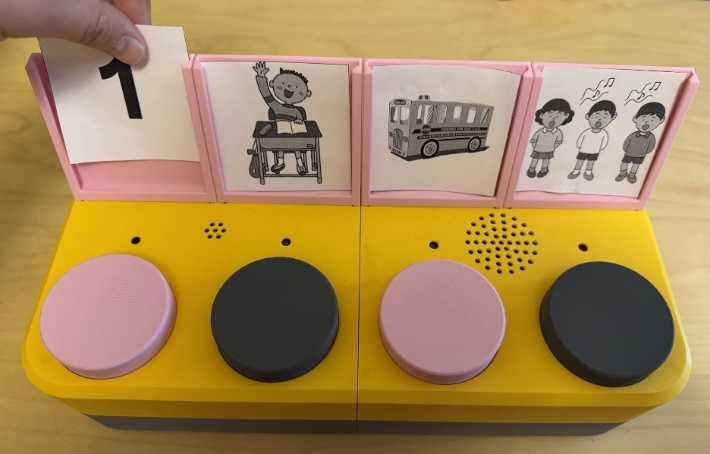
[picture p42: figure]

## Basic Function

- Record your own messages at each message position, using the record mode and direct access switches
- Start switch scanning with the assistive switch connected to the “SELECT” port
- First message will start playing, followed by a delay (controlled by the “SPEED” switch
- After the delay, the next message will start playing, if the user does not select that message
- To select a message, activate the “SELECT” switch again anytime the message is playing or during the delay
- Playback stops after a message is replayed, or the delay times out after the last message

## Using the Chatterbox

Slide the power switch to “ON” to turn the Chatterbox on. Slide the Mode switch to the desired mode (Record or Playback). The following table explains what each input does based on the mode the Chatterbox is in.

Input | Record Mode | Playback Mode
Slide Level switch | Select the message level to record or play back.
Press direct access switch | Play message recorded at that position.
Hold direct access switch (>1 second) | Delete existing message and record new message at that position. Recording starts when only that LED starts blinking and continues while the switch is held. | Play back message recorded at that position after the switch is released.
Activate assistive switch in “SELECT” port | No function. | If not already switch scanning: Start switch scanning. If already switch scanning: Replay current message.
Activate assistive switch in “NEXT” port | No function. | If not switch scanning: No function. If switch scanning: Advance to the next message.
Slide “SPEED” switch | No function. | Change the delay between messages when switch scanning. Preset delay times are 2, 4, and 6 seconds.
Turn volume knob | Change volume (counterclockwise = decrease, clockwise = increase)

## LEDs

LED Behaviour | Meaning
All four LEDs blinking | Chatterbox is in Record mode
All LEDs off | Chatterbox is off or in Playback mode
One LED blinking | Recording message in the corresponding position
One LED on | Message playing in corresponding position, or indicating message position that will be played (during delay)
First two LEDs blinking | Micro SD card is not inserted into SD card reader

## Troubleshooting

If the Chatterbox exhibits any unexpected behaviour, or is not responding to inputs, turn it off and on again.

## Support

For support, contact the maker of your device or Makers Making Change at info@makersmakingchange.com

© 2025 by OR Neil Squire. This work is licensed under the CC BY SA 4.0 License: http://creativecommons.org/licenses/by-sa/4.0 Files available at makersmakingchange/Chatterbox: A switch scanning AAC device for users with visual impairment. Page 2 of 3

V1.0 | March 2026 Chatterbox Quickstart Guide

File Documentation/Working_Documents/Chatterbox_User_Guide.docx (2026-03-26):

# Overview

This document contains the necessary information to use the Chatterbox. The Chatterbox is a switch scanning communication device which provides auditory feedback to guide the user while scanning.

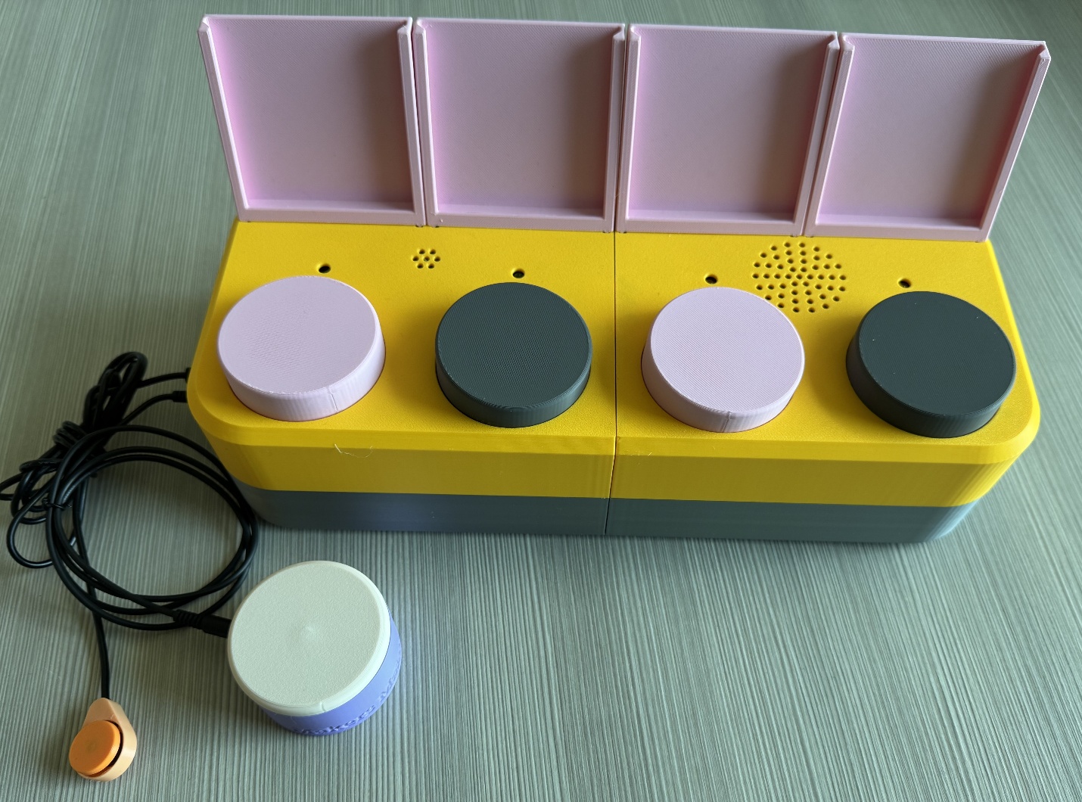
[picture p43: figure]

## Introduction

The Chatterbox is an Augmented and Alternative Communication (AAC) device that allows users to play pre-recorded messages using single or dual switch scanning. The Chatterbox provides auditory and visual feedback to indicate the message a user can play. The Chatterbox is meant for users with complex communication needs and visual impairment.

## Features

The following pictures show the different features of the Chatterbox. The features and their functions are described in the table following the images.

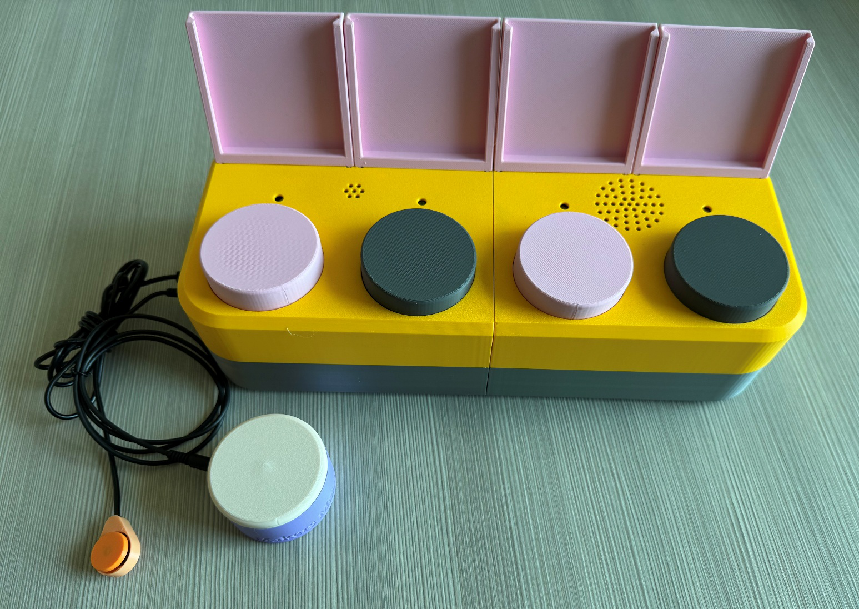
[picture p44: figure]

Assistive Switches for switch scanning (not included with device unless requested)

Direct access switches

Speaker

Mic

Message LEDS

Label holders

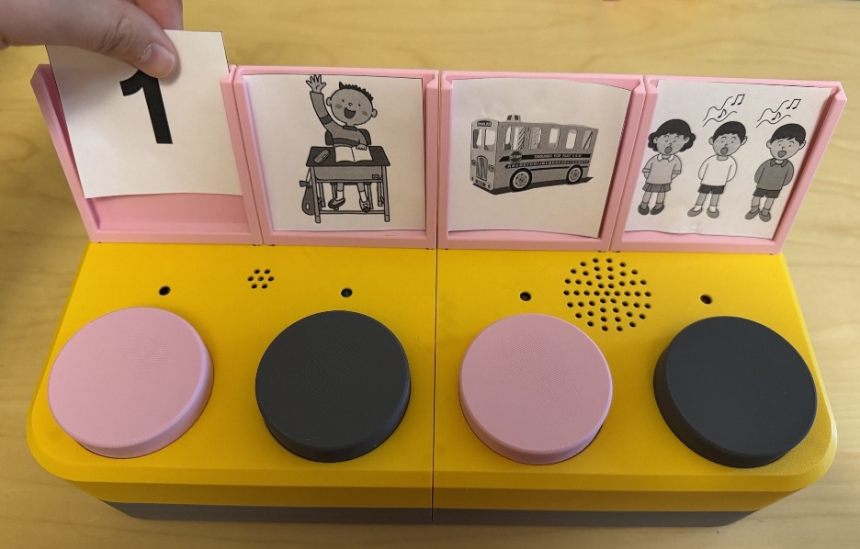
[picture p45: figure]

### Front/Top of the Chatterbox

Feature | Function
Label holders | Hold customized labels above each switch to represent the message recorded at that switch.
Message LEDs | - Indicate which message is playing/will be selected while switch scanning (when lit) - Indicate if the device is in Record Mode (when all four are flashing) - Indicate which message is being recorded (when flashing)
Speaker | Holes above the speaker to allow sound to escape the enclosure more easily.
Mic (microphone) | Holes above the microphone which is used when recording new messages.
Direct Access Switches | - Play a specific message without switch scanning (when pressed in Playback or Record Mode) - Record a message (while held in Recording Mode)
Assistive Switches for switch scanning | - Start switch scanning (SEL switch) - Select the message to play back (SEL switch) - Advance to the next message (NXT switch) Note: The switches pictured are for demonstration purposes. They are not included with the Chatterbox and can be any switch that uses a 3.5mm mono cable.

### Side of the Chatterbox

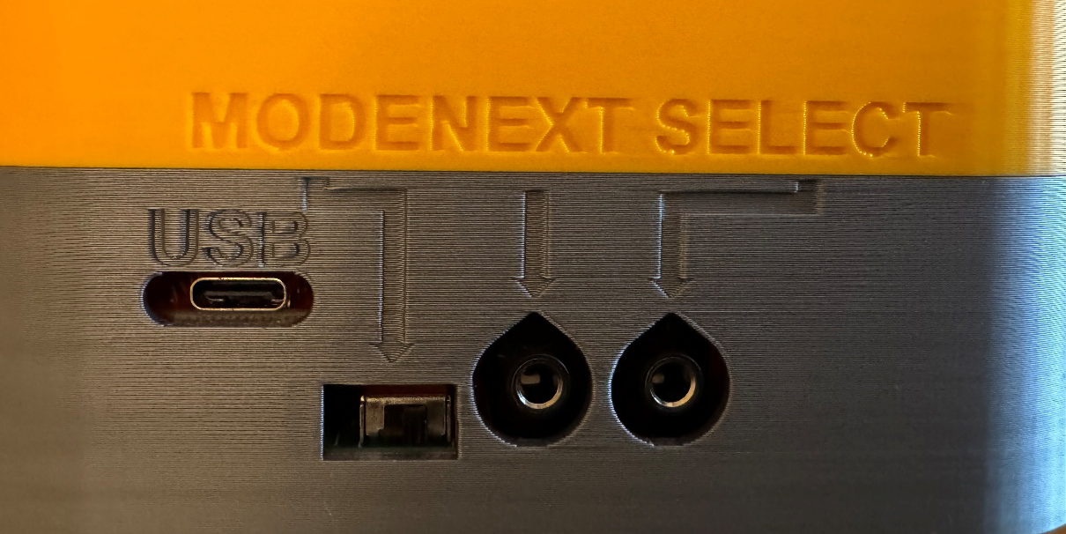
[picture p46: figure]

Feature | Function
SELECT assistive switch port | - Start switch scanning - Select current message to play back This port must be used for single or dual switch scanning.
NEXT assistive switch port | - Advance to the next message This port is required only if the user wants to use dual switch scanning.
USB Port | - Access to microcontroller’s USB-C port for reprogramming. - Power device from USB (if desired)
MODE Switch | Change between Playback and Recording modes.

### Back of the Chatterbox

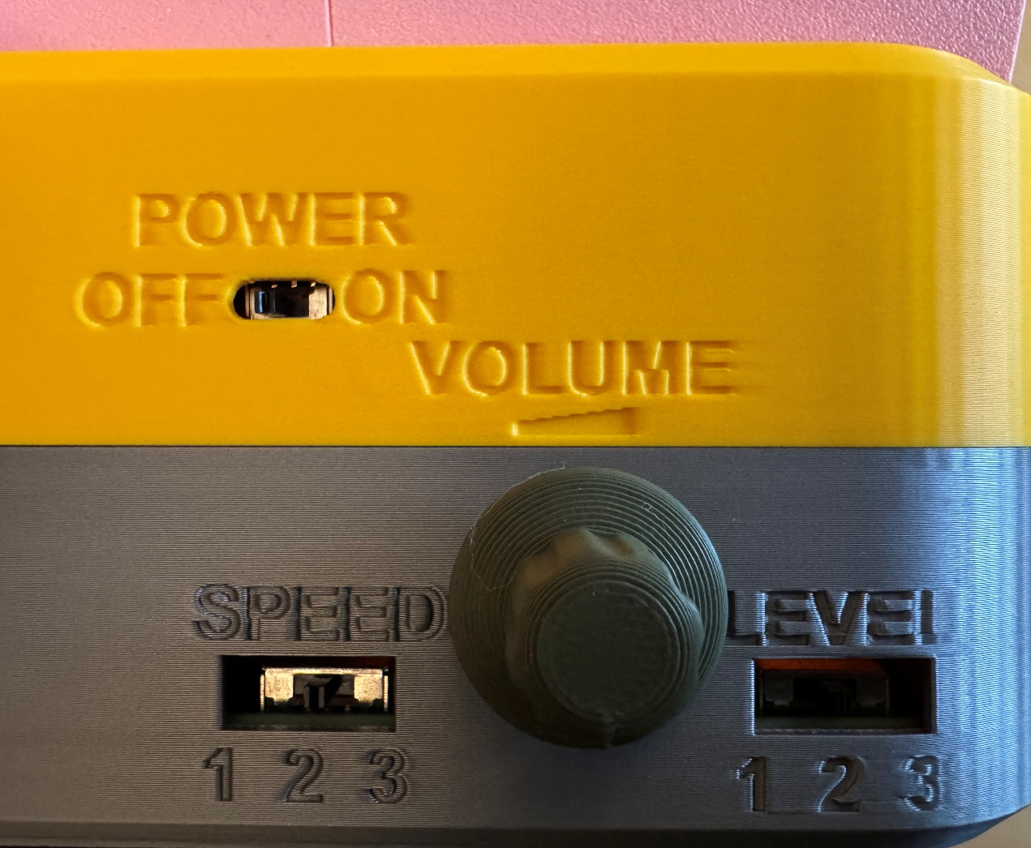
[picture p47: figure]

Feature | Function
Power Switch | - Turn the Chatterbox on or off. - Not required if powering the device with USB.
Level Switch | Change between message levels (three positions and three levels).
Volume knob | Adjust the volume of message playback.
Speed Switch | Change between different pre-set delay times between messages while switch scanning. (Three positions and three speeds). The pre-set delays are 3, 5, and 7 seconds. These can be changed in the Chatterbox firmware.

### Bottom of the Chatterbox

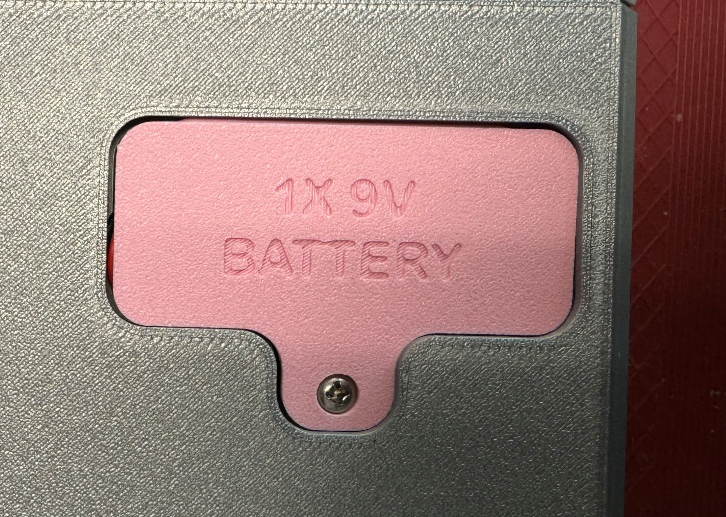
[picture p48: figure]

Feature | Function
Battery holder (on the bottom of the device) | - Holds the battery inside the Chatterbox - Prevents accidental access to the battery

### Direct Access Switches

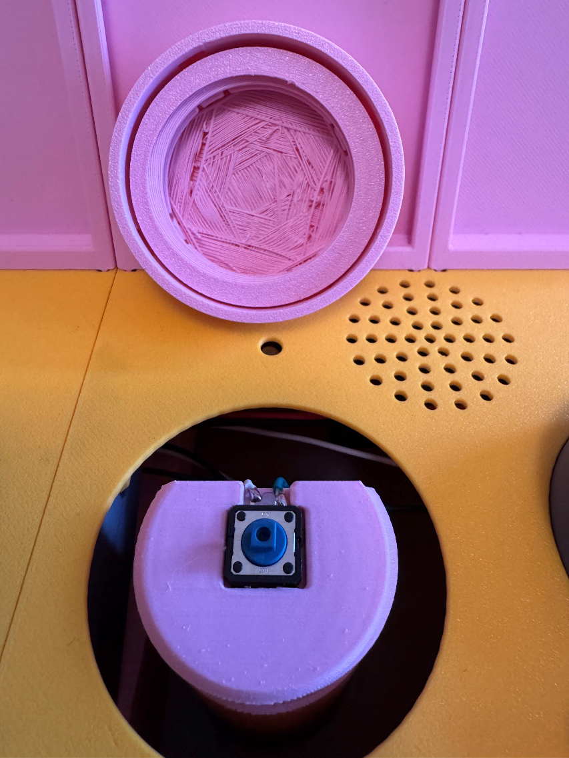
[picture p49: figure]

Swappable switch cap

Switch base

Feature | Function
Swappable switch cap | - Screw-on switch cap that can be changed to customize the top of each direct access switch
Switch base | - Threaded base that holds different screw-on switch caps.

## Specifications

Item | Chatterbox
Size (Length x Width x Height) [mm] | 330 x 140 x 80 (main enclosure body only) 330 x 156 x 150 (including label holders and volume knob)
Mass [g] | 884
Visible area of label (Length x Width) [mm] | 70.6 x 70.2
Maximum label dimensions (Length x Width x Thickness) [mm] | 71.6 x 71.2 x 1.5

## Compatibility

The Chatterbox uses two 3.5mm mono jacks to connect up to two assistive switches to operate the switch scanning function. Any assistive switch with a 3.5mm mono cable can be used with the Chatterbox.

## Usage

### Powering the Chatterbox

The Chatterbox runs on a 9V battery. If the device does not turn on or is not functioning properly, check the battery is connected properly. You can access the battery through the battery holder on the bottom of the device. You will need a Phillips head (+ shaped) screwdriver to remove the screw that keeps the holder shut.

You can also run the Chatterbox through the USB port on the side. This can be plugged into a computer/laptop, a wall adapter, or a USB battery bank. DO NOT USE BOTH THE 9V BATTERY AND USB PORT AT THE SAME TIME TO POWER THE CHATTERBOX. Remove the 9V battery, or make sure the power switch is set to “OFF” before plugging into USB power. Using the 9V battery and the USB port at the same time could damage the Chatterbox, or the computer it is plugged into.

### Initial Setup

Messages need to be recorded on the Chatterbox before it can be used for switch scanning communication. The process to record messages is outlined in the next section. Once the messages are recorded, the Chatterbox should be placed in front of the user facing them, as seen below. The Chatterbox should be positioned so the user can see the message LEDs above each direct access switch, in case they have partial sight.

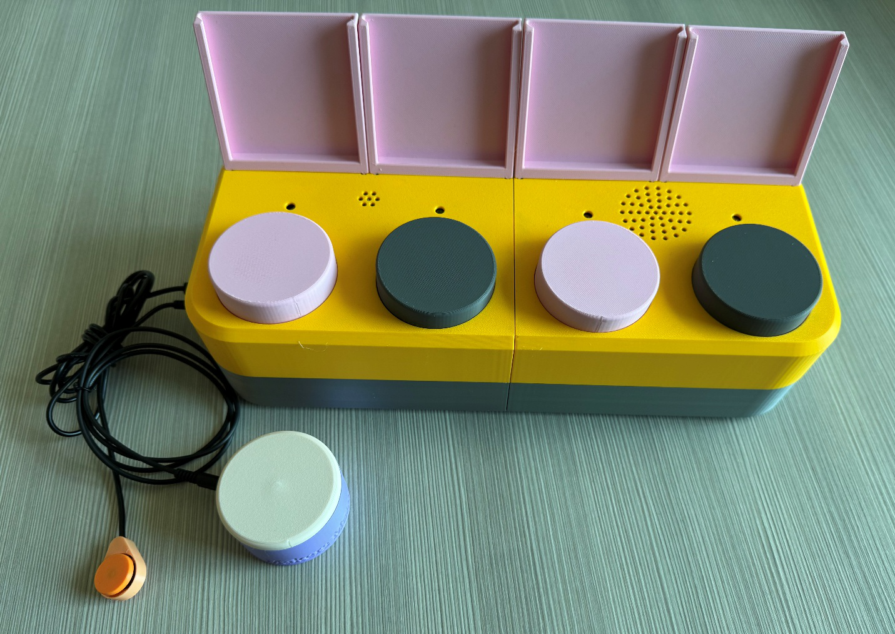
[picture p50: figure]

The Chatterbox can be used on a user’s wheelchair tray, on a desk/table, or any other flat surface that is large enough to hold it. If the user is moving around with the Chatterbox, or is expected to be pushing on it during use, you may want to place it on a non-slip surface, such as a Dycem mat, or hook-and-loop tray.

The Chatterbox can be used with any assistive switch that has a 3.5mm mono cable connection, and these switches can be plugged into the ports at the side of the device. The switches should be chosen to suit the user’s needs, and mounted appropriately for their abilities.

### Regular Use

#### Recording new messages

1. Turn on the Chatterbox.
  a. If using the 9V battery: slide the POWER switch to the ON position
  b. If powering through the USB: plug the Chatterbox into a power source (laptop/computer, USB charger, power bank, etc.) with a USB-C cable.
2. Use the MODE switch to change to Recording Mode (if the device is not already in Recording Mode). Recording Mode is indicated by all four message LEDs flashing.
3. Use the LEVEL switch to adjust to the message level you would like to change.
4. Hold down the direct access switch for the message you would like to record. When only the corresponding message LED is flashing the device has started recording.
5. While holding down the direct access switch, speak or play audio clearly into the mic holes.
6. Once the message is recorded, release the direct access switch. All four message LEDS should start flashing.

You can play a recorded message at any time in Recording Mode by pressing a direct access switch. This can be useful to listen to test a message playback before changing modes, or to identify the messages already recorded on the device.

#### Playing messages with direct access switches

1. Turn the Chatterbox on.
  a. If using the 9V battery: slide the POWER switch to the ON position
  b. If powering through the USB: plug the Chatterbox into a power source (laptop/computer, USB charger, power bank, etc.) with a USB-C cable.
2. Regardless of mode, press the direct access switch for the message you would like to play.

#### Single switch scanning

1. Plug an assistive switch into the SELECT assistive switch port.
2. Turn the Chatterbox on.
  a. If using the 9V battery: slide the POWER switch to the ON position
  b. If powering through the USB: plug the Chatterbox into a power source (laptop/computer, USB charger, power bank, etc.) with a USB-C cable.
3. Use the MODE switch to change to Playback Mode (if the device is not already in Playback Mode). All message LEDS will be off unless a message is being played, or switch scanning has started in Playback Mode.
4. Use the LEVEL switch to select the message level you would like to play back.
5. Use the SPEED switch to select the delay time between messages.
6. Press the assistive switch plugged into the SELECT assistive switch port to start switch scanning. The first message on the selected level will play, and the message LED will light up.
7. If the user wants to advance to the next message, they must wait for the pre-selected delay time to run out. The message LED will remain lit until the next message starts playing.
8. Press the assistive switch again to replay/select a message. A message can be selected at any time while its corresponding message LED is lit. If the message is selected while it is still playing, the message will start from the beginning.
9. The Chatterbox will automatically exit switch scanning if it runs out of messages, or after it has played the message the user selected. Switch scanning always starts from the first message on the selected message level.

#### Dual switch scanning

1. Plug an assistive switch into the NEXT assistive switch port.
2. Follow the steps for single switch scanning.
3. To advance to the next message while switch scanning, press the assistive switch plugged into the NEXT assistive switch port. If the NEXT switch is pressed while a message is playing, the message will stop, and the next message will start playing.
4. The Chatterbox will automatically exit switch scanning if it runs out of messages or after it has played the message the user selected. Switch scanning always starts from the first message on the selected message level.

#### Changing switch caps

1. While pulling gently up on the switch cap, twist it counterclockwise to unscrew it.
2. Twist the new switch cap clockwise onto the base. The cap is designed to not tighten down and stop twisting to avoid over-tightening. The cap should be able to spin freely on the base without falling off, and should activate the switch when pressed.

#### Creating and adding message labels

You can make custom labels for the messages. These labels can be held in the label holders behind each message LED. The labels must fit in the box below, which is 71x71 mm.

Labels can be created on the computer, printed on paper, and cut to size. They can also be drawn on pieces of paper that are no larger than 71x71 mm. If creating 3D printed labels, they can be no thicker than 1.3 mm to slide in and out of the label holders.

1. Create labels.
2. Slide label into corresponding label holder.
3. To change labels, slide the existing label out of the holder and replace it with the new label.

### Takedown / Storage

When not in use, the Chatterbox should be stored in a cool place out of direct sunlight.

## Switch cap customization

The switch caps can also be customized to help label the messages. We have outlined three potential methods to customize the switch caps.

#### Hook and loop fastener

Hook and loop fastener can be used to quickly switch different materials on the button caps. The loop part of the hook and loop fastener can be attached to the button caps and the hook side attached to whatever you would like to attach to the button cap. These could include different materials for tactile identification or printed paper labels.

We would recommend this option for anyone who is regularly switching and reusing different custom switch toppers, and want to use a variety of materials on the switch toppers.

#### Glue

Glue can permanently attach different materials to the top of the switch caps. Glue offers the same customizability as the hook and loop fastener, but creates a permanent attachment. Swapping the custom toppers would require having a different 3D printed button cap for each custom top.

We would recommend this option for anyone who uses a small set of custom tops and wants to use a variety of materials on the switch caps.

#### Custom 3D printed topper

Different symbols, patterns, and textures can be added to the CAD file of the switch caps, like is done with the MMC60 and Interact Switches. These symbols, patterns, and textures would be permanently attached to the switch cap, and can be printed in different colours, but cannot be done in different materials to the rest of the cap. The image below shows an example of a pattern someone could create on a customized 3D printed topper.

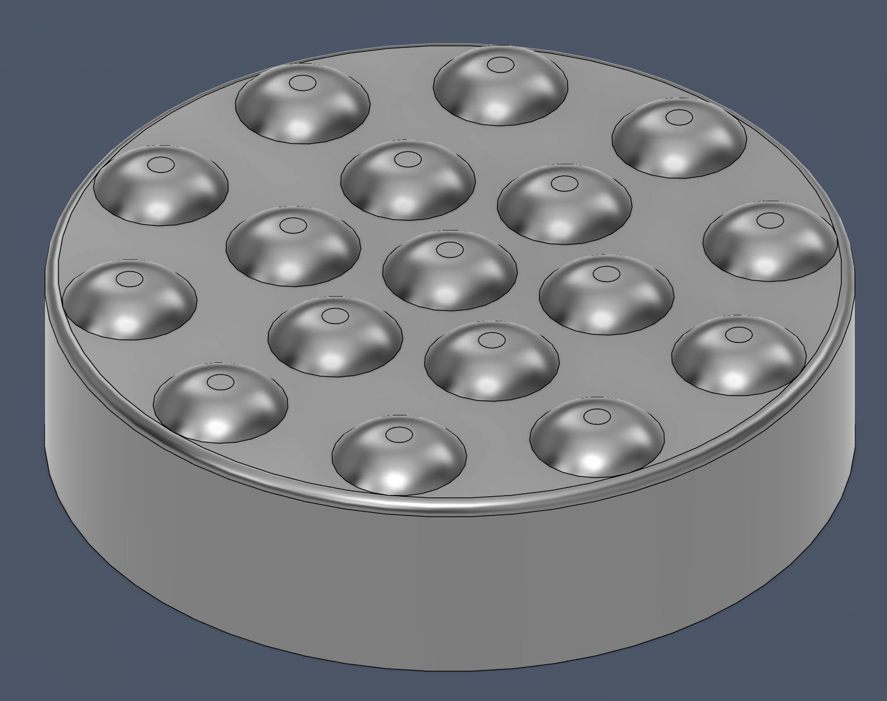
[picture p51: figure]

We recommend this option for someone who uses the same small set of custom tops regularly.

## Cleaning

The Chatterbox can be wiped with a damp cloth and any cleaner that does not harm plastic.

## Care

The Chatterbox is made of 3D printed plastic. Exposure to high heat may cause warping and/or negatively affect function. Extended exposure to sunlight will also weaken the plastic on the device.

The Chatterbox contains electronics and is not waterproof. If the device becomes wet, make sure it is off and do not use it until it has completely dried. It may help to open the enclosure to speed up drying and ensure it has completely dried.

## Disposal

PLA filament may be industrially compostable in your area. Check with your waste management company if PLA can be composted or must be thrown in the garbage.

Disassemble the Chatterbox and separate out the recyclable and compostable components, and those that must be thrown out. Electronics and batteries should be disposed of following your local waste management guidelines.

© 2025 by Neil Squire. This work is licensed under the CC BY SA 4.0 License: http://creativecommons.org/licenses/by-sa/4.0 Files available at makersmakingchange/Chatterbox: A switch scanning AAC device for users with visual impairment. Page 2 of 3

V1.0.0 | March 2026 Chatterbox user Guide

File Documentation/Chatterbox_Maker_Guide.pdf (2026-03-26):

V1.0.0 | October 2025

## Chatterbox

## MAKER GUIDE

© 2025 by Neil Squire. (https://neilsquire.ca/)
This work is licensed under the CC BY SA 4.0 License: http://creativecommons.org/licenses/by-sa/4.0
Files available at https://github.com/makersmakingchange/Chatterbox | Page 1 of 103

### Overview

This document contains the necessary information to build the Chatterbox. The Chatterbox is a switch scanning communication device which provides auditory feedback to guide the user while scanning.

## MAKER GUIDE

Files available at https://github.com/makersmakingchange/Chatterbox | Page 2 of 103

### Contents

Overview | 1
Maker Checklist | 5
Maker To Do List | 5
Items to Give to User | 5
Tool List | 6
Tools / Equipment | 6
Supplies | 6
Personal Protective Equipment (PPE) | 6
Customization Guide | 7
Custom Printed Circuit Board (PCB) Guide | 7
Ordering the Custom PCBs | 7
3D Printing Guide | 9
3D Printing Summary | 9
3D Printing Settings | 9
Post-Processing | 10
Examples of Quality Prints | 10
Maker Component List | 12
Assembly Guide | 19
Part A: Main PCB | 20
Part A: Required Components | 20
Part A: Required Tools and Supplies | 22
Part A: Required Personal Protective Equipment (PPE) | 22
Soldering Image Guide | 22
Part A: Main PCB Assembly Steps | 23
Part B: Secondary PCB | 48
Part B: Required Components | 48
Part B: Required Tools and Supplies | 50
Part B: Required Personal Protective Equipment (PPE) | 50

## MAKER GUIDE

Files available at https://github.com/makersmakingchange/Chatterbox | Page 3 of 103
Part B: Secondary PCB Assembly Steps | 50
Part C: LED PCBs | 68
Part C: Required Components | 68
Part C: Required Tools and Supplies | 69
Part C: Required Personal Protective Equipment (PPE) | 69
Part C: LED PCB Assembly Steps | 69
Part D: Enclosure Assembly | 75
Part D: Required Components | 75
Part D: Required Tools and Supplies | 77
Part D: Required Personal Protective Equipment (PPE) | 77
Part D: Enclosure Assembly Steps | 77
Part E: Flashing Firmware to the Chatterbox | 96
Part E: Required Components | 96
Part E: Required Tools and Supplies | 96
Step E-01: Connect the Chatterbox to the Computer | 96
Step E-02: Setup Arduino IDE on Computer | 96
Step E-03: Setup Arduino IDE for the Seeeduino Nano | 96
Step E-04: Install Libraries | 97
Step E-05: Enable Recording | 97
Step E-06: Setup Local Code Directory | 98
Step E-07: Flash Firmware to the Chatterbox | 98
Testing | 98
Battery Power | 99
Mode Switch | 100
Record Messages | 100
Level Switch | 100
Message Playback | 100
Switch Scanning | 101
Next Switch | 101
Speed Switch | 101

## MAKER GUIDE

Files available at https://github.com/makersmakingchange/Chatterbox | Page 4 of 103
Volume | 102
Troubleshooting | 102
When powered, the first two lights start blinking and nothing else will happen | 102
Chatterbox does not turn on with battery, but did on USB-C power | 102
An LED does not turn on | 102

When a button is pressed, the corresponding LED turns on very briefly but nothing else happens...103

The Chatterbox seems to skip playing a message while switch scanning, and goes right to the delay
between messages | 103
Nothing happens when I press a message button | 103
Nothing happens when I press the assistive switch attached to the Select jack | 103
Nothing happens when I press the assistive switch attached to the Next jack | 103

## MAKER GUIDE

Files available at https://github.com/makersmakingchange/Chatterbox | Page 5 of 103

### Maker Checklist

This list provides an overview of the steps required to build and deliver the Chatterbox

### Maker To Do List

Read through the Maker Guide to become familiar with required components, tools, supplies, safety gear, and overall assembly steps.
Talk to the User about customization options
- What colour(s) would they like the Chatterbox printed in.
- If they would like contrast between the direct access switches and top of the enclosure.
- If they would like any custom caps, or the regular flat top on the direct access switches.
- How they would like to receive the “User Guide” (PDF or physical copy)
- Ask if they would like the label holders connected or if they can connect them (having the label holders connected before shipping may make shipping more difficult)
Order custom PCBs
Order hardware components
- Please see the Bill of Materials (BOM) for links to purchase, and quantities for each component
Gather tools, supplies, and safety equipment.
Assemble the device
Flash firmware to the Chatterbox
Test the Chatterbox
Print “User Guide” (if the User would like a physical copy)

### Items to Give to User

Assembled Chatterbox in enclosure
Label holders
User Guide

## MAKER GUIDE

Files available at https://github.com/makersmakingchange/Chatterbox | Page 6 of 103

### Tool List

### Tools / Equipment

Tool ID | Description | Required / Recommended | Notes
T01 | Soldering iron | Required | Soldering components
T02 | Flush cutters | Required | Trimming electronic components
T03 | Wire strippers | Required | Stripping insulation off wires
T04 | Phillips head screwdriver (#2) | Required | Assembling the Chatterbox
T05 | Precision flathead screwdriver (2.5mm or smaller) | Required | Securing the speaker to the amp
T06 | Two assistive switches | Required | For testing the switch scanning functionality of the Chatterbox

### Supplies

Supplies ID Description | Quantity | Notes
S01 | Solder | - | Soldering components together
S02 | Hot glue or super glue | - | Holding the direct access switches in place

### Personal Protective Equipment (PPE)

PPE ID | Description | Notes
P01 | Safety goggles | Trimming electrical components and soldering may cause flying debris, which could harm your eyes if not wearing safety glasses.

## MAKER GUIDE

Files available at https://github.com/makersmakingchange/Chatterbox | Page 7 of 103

### Customization Guide

The device can be printed in the user’s desired colour(s). We recommend printing the enclosure top and button caps in colours with high contrast (ex: white and black) to make it easier for users with partial vision to locate the buttons, if they desire. You may also print each button cap in a different colour to more easily distinguish between the buttons.

### Custom Printed Circuit Board (PCB) Guide

The Chatterbox uses three (3) custom printed circuit boards.

The custom PCBs can be ordered from one of a variety of PCB Manufacturers. Typically, the minimum quantity for a custom PCB is five. Shipping options vary significantly in cost and shipping time. Plan on at least a week from the time of order to the PCBs arrival.

### Ordering the Custom PCBs

1. Select a PCB Fabrication Company
a. JLPCB (https://jlcpcb.com/)
b. PCBWay (https://www.pcbway.com/)
c. OSH Park (https://oshpark.com/)
d. Seeed Fusion PCB (https://www.seeedstudio.com/fusion_pcb.html)
2. Create an account or use a guest login.
3. Upload the Gerber Files (e.g., Chatterbox_Main_PCB.zip).
4. Select the fabrication options:
a. PCB Layers: 2 Layers
b. PCB Quantity:
i. Main PCB: 5 boards
ii. Secondary PCB: 5 boards iii. LED PCB: 20 boards*
c. PCB Thickness: 1.6 mm
d. Surface Finish: HASL with lead
e. PCB Colour: Choose what you like. Note that certain colours may impact build time and cost.
f. The default settings for the other settings should work.
5. Select shipping option.
a. Shipping options and costs vary significantly. Select the best option based on your budget and timing.
6. Submit the order.

## MAKER GUIDE

Files available at https://github.com/makersmakingchange/Chatterbox | Page 8 of 103

*Note: we recommend ordering 20 LED PCBs as each Chatterbox requires four (4) LED boards. Ordering 20 boards lets you build up to five Chatterboxes on one PCB order, and the cost of 20 boards instead of 5 is negligible.

## MAKER GUIDE

Files available at https://github.com/makersmakingchange/Chatterbox | Page 9 of 103

### 3D Printing Guide

The device was originally printed on a Bambu P1S with Bambu Studio, with the default slicer profile.

### 3D Printing Summary

Metrics | Single Unit
Total Print Time (hour min) | 29h 12m
Total Number of Components | 32
Typical Total Mass (g) | 658
Typical Number of Print Setups | 8

### 3D Printing Settings

Note that the 3D printing material should be assumed to be PLA unless otherwise noted in the table below. The masses and print time are the total for each part (ex: each Label_Holder.stl weighs 19g, so all four are listed as 76 g).

Print File Name | Qty | Total Print Time (hr:min) | Mass (g) | Infill (%) | Support (Y/N) | Layer Height/ Nozzle Diameter(mm) | Notes
Enclosure_Bottom _Left.stl | 1 | 2:49 | 106 | 20 | N | 0.2/0.4
Enclosure_Bottom _Right.stl | 1 | 2:32 | 109 | 20 | N | 0.2/0.4
Enclosure_Top_Lef t.stl | 1 | 2:17 | 89 | 20 | N | 0.2/0.4
Enclosure_Top_Rig ht.stl | 1 | 2:17 | 86 | 20 | N | 0.2/0.4
Label_Holder.stl | 4 | 2:04 | 76 | 20 | N | 0.2/0.4
Button_Base.stl | 4 | 2:44 | 104 | 20 | N | 0.2/0.4
Button_Cap.stl | 4 | 1:48 | 52 | 20 | N | 0.2/0.4
Button_Insert.stl | 4 | 1:28 | 28 | 20 | N | 0.2/0.4
Center_Support.stl | 2 | 1:38 | 48 | 20 | N | 0.2/0.4
Slide_Switch_Cover .stl | 4 | 0:09 | 1 | 20 | N | 0.2/0.4
Slide_Switch_Cover _Pin.stl | 4 | 0:07 | 1 | 20 | N | 0.2/0.4
Volume_Knob.stl | 1 | 0:13 | 2 | 20 | N | 0.2/0.4
Battery_Cover.stl | 1 | 0:20 | 7 | 20 | N | 0.2/0.4

## MAKER GUIDE

Files available at https://github.com/makersmakingchange/Chatterbox | Page 10 of 103

### Post-Processing

Inspect the 3D printed parts for any printing defects, sharp edges, or burrs. Sharp edges and burrs can be removed with sanding or deburring tools.

### Examples of Quality Prints

Compare your 3D prints to the images here. If there are significant differences, you may need to reprint the part.

Chatterbox Enclosure
Enclosure_Bottom_Left.stl | Enclosure_Bottom_Right.stl | Enclosure_Top_Left.stl
Enclosure_Top_Right.stl | Label_Holder.stl | Button_Base.stl
Button_Cap.stl | Button_Insert.stl | Center_Support.stl

## MAKER GUIDE

Files available at https://github.com/makersmakingchange/Chatterbox | Page 11 of 103
Battery_Holder.stl | Volume_Knob.stl | Slide_Switch_Cover.stl

Slide_Switch_Cover_Pin.stl

## MAKER GUIDE

Files available at https://github.com/makersmakingchange/Chatterbox | Page 12 of 103

### Maker Component List

Main PCB
A01 | Main PCB | QTY: 1 | A02 | 2.2k Ohm resistor | QTY: 8 | A03 | 10uF Capacitor | QTY: 1
| | | Note: The resistor body colour may change, but the bands will be the same. | | | Note: The capacitor may be labelled with 106, 10u, or may be a different colour.
A04 | Two position switch | QTY: 1 | A05 | Three position switch | QTY: 2 | A06 | 8 position female header | QTY: 1
A07 | 15 position
female
header
QTY: 2 | A08 | 3.5mm jack | QTY: 2 | A09 | Ribbon cable connector

QTY: 1

A10 Seeeduino
Nano
QTY: 1 | A11 | Micro SD
card reader
QTY: 1 | A12 | 512 MB
Micro SD
Card

QTY: 1

## MAKER GUIDE

Files available at https://github.com/makersmakingchange/Chatterbox | Page 13 of 103
A13 | 24 AWG
wire

QTY:
166 cm

A14 10 kOhm
Logarithmic
Potentiome
ter

QTY: 1

Secondary PCB
B01 Secondary
PCB
QTY: 1 | B02 | 10uF
Capacitor
QTY: 2 | B03 | Two
position
switch

QTY: 1

## MAKER GUIDE

Files available at https://github.com/makersmakingchange/Chatterbox | Page 14 of 103
| Note: The capacitor may be labelled with 106, 10u, or may be a different colour.

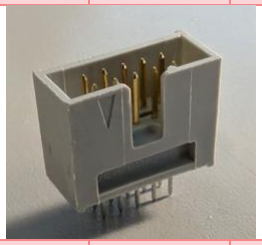
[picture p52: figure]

B04 | 5 position female header | QTY: 2 | B05 | 9V battery clip | QTY: 1 | B06 | Ribbon cable connector | QTY: 1
B07 | Amp | QTY: 1 | B08 | Microphone | QTY: 1 | B09 | 24 AWG wire

QTY:
124
cm
B10 | Speaker | QTY: 1

## MAKER GUIDE

Files available at https://github.com/makersmakingchange/Chatterbox | Page 15 of 103

LED PCBs
C01 | LED PCB | QTY: 4 | C02 | 2.2k Ohm resistor | QTY: 4 | C03 | 5mm LED | QTY: 4
| | | Note: The resistor body colour may change, but the bands will be the same.
C04 | Completed Secondary PCB | QTY: 1

## MAKER GUIDE

Files available at https://github.com/makersmakingchange/Chatterbox | Page 16 of 103

Enclosure
D01 Enclosure
Bottom -
Left
QTY: 1 | D02 | Enclosure
Bottom -
Right
QTY: 1 | D03 | Assembled
Main PCB

QTY: 1

D03 #4x3/8”
machine
screw
QTY: 20 | D04 | Centre
support
QTY: 2 | D05 | Button base | QTY: 4

## MAKER GUIDE

Files available at https://github.com/makersmakingchange/Chatterbox | Page 17 of 103
D07 | Tactile
switch
QTY: 4 | D08 | Enclosure
Top - Left
QTY: 1 | D09 | Enclosure
Top - Right

QTY: 1

D10 Ribbon
Cable
QTY: 1 | D11 | Assembled
Secondary
PCB and LED
PCBs
QTY: 4 | D12 | Button
insert

QTY: 4

D13 | Button cap | QTY: 4 | D14 | Label holder | QTY: 4 | D15 | 9V battery | QTY: 1

## MAKER GUIDE

Files available at https://github.com/makersmakingchange/Chatterbox | Page 18 of 103
D16 | Battery
Cover
QTY: 1 | D17 | Volume
knob
QTY: 1 | D18 | Slide Switch
Cover

QTY: 4

D19 Slide Switch Cover Pin

QTY: 4

## MAKER GUIDE

Files available at https://github.com/makersmakingchange/Chatterbox | Page 19 of 103

### Assembly Guide

Assembly Section
Part A: Main PCB

Part B: Secondary PCB

## MAKER GUIDE

Files available at https://github.com/makersmakingchange/Chatterbox | Page 20 of 103

Part C: LED PCBs

Part D: Enclosure
Assembly

Part E: Flashing Firmware

### Part A: Main PCB

Part A: Required Components
Main PCB
A01 | Main PCB | QTY: 1 | A02 | 2.2k Ohm resistor
QTY: 8 | A03 | 10uF
Capacitor

QTY: 1

## MAKER GUIDE

Files available at https://github.com/makersmakingchange/Chatterbox | Page 21 of 103
| Note: The resistor body colour may change, but the bands will be the same. | Note: The capacitor may be labelled with 106, 10u, or may be a different colour.
A04 | Two position switch | QTY: 1 | A05 | Three position switch | QTY: 2 | A06 | 8 position female header | QTY: 1
A07 | 15 position
female
header
QTY: 2 | A08 | 3.5mm jack | QTY: 2 | A09 | Ribbon cable connector

QTY: 1

A10 Seeeduino
Nano
QTY: 1 | A11 | Micro SD
card reader
QTY: 1 | A12 | 512 MB
Micro SD
Card

QTY: 1

## MAKER GUIDE

Files available at https://github.com/makersmakingchange/Chatterbox | Page 22 of 103
A13 | 24 AWG
wire

QTY:
166 cm

A14 10 kOhm
Logarithmic
Potentiome
ter

QTY: 1

Part A: Required Tools and Supplies
- Soldering Iron
- Solder
- Wire cutters/strippers
- Flush cutters

Part A: Required Personal Protective Equipment (PPE)
- Safety glasses/goggles

Soldering Image Guide
You can refer to this image guide throughout Parts A-C to check the quality of your solder joints.

## MAKER GUIDE

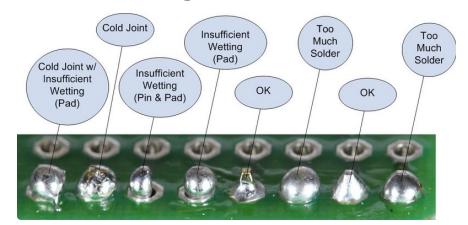
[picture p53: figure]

Files available at https://github.com/makersmakingchange/Chatterbox | Page 23 of 103

The above image is from Adafruit’s soldering guide. (https://cdn-learn.adafruit.com/downloads/pdf/adafruit-guide-excellent-soldering.pdf)

Part A: Main PCB Assembly Steps
All electrical components will be inserted from the “Front” side of the board, and all soldering will be done on the “Back” side of the board.

Step A-01: Add resistors to PCB
Insert the resistors (A02) into the spaces labeled R2-R8 on the Main PCB (A01). Make sure the resistors are lying flat on the board, and bend the leads to hold the resistors in place.

## MAKER GUIDE

Files available at https://github.com/makersmakingchange/Chatterbox | Page 24 of 103

Step A-02: Solder and trim all resistor leads
Solder both leads of each resistor to the PCB. Once the leads are soldered, trim the excess wire off using the flush cutters.

## MAKER GUIDE

Files available at https://github.com/makersmakingchange/Chatterbox | Page 25 of 103

Step A-03: Insert capacitor
Insert the capacitor (A03) into the position labeled “C1” on the Main PCB. Make sure the capacitor sits flush to the PCB, then bend the leads to hold the capacitor in place.

## MAKER GUIDE

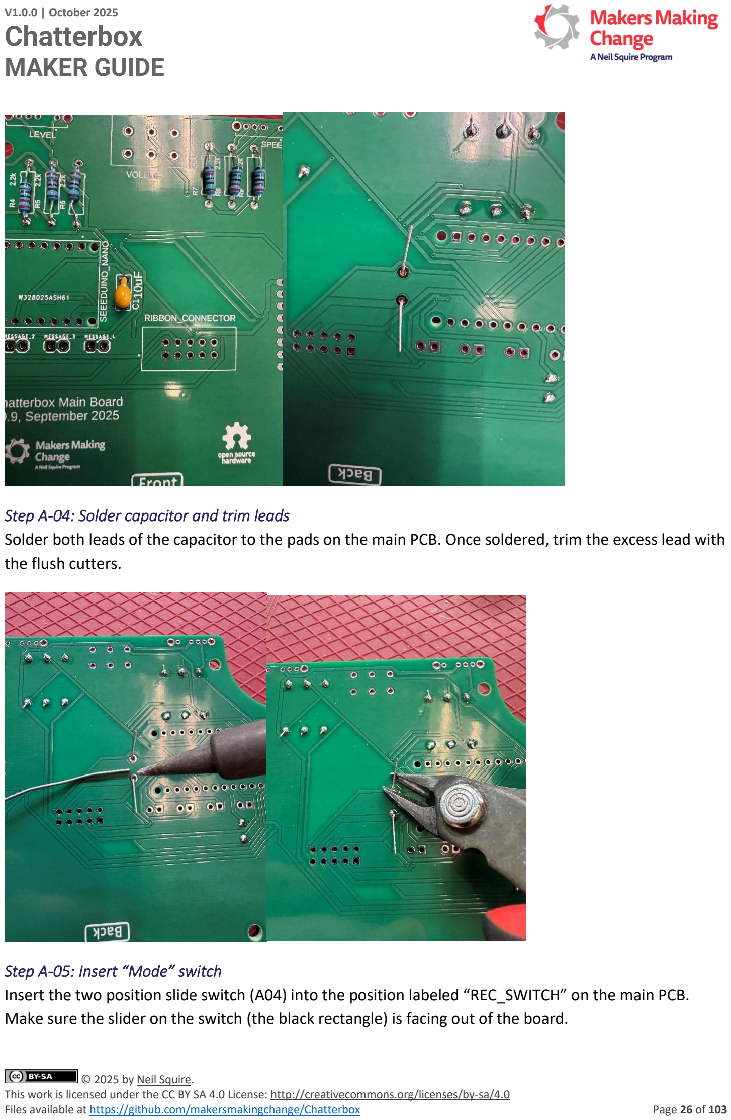
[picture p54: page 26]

Files available at https://github.com/makersmakingchange/Chatterbox | Page 26 of 103

Step A-04: Solder capacitor and trim leads
Solder both leads of the capacitor to the pads on the main PCB. Once soldered, trim the excess lead with the flush cutters.

Step A-05: Insert “Mode” switch
Insert the two position slide switch (A04) into the position labeled “REC_SWITCH” on the main PCB. Make sure the slider on the switch (the black rectangle) is facing out of the board.

## MAKER GUIDE

Files available at https://github.com/makersmakingchange/Chatterbox | Page 27 of 103

Step A-06: Solder one switch lead and check alignment
Solder one of the three leads of the two position slide switch to the main board. Double check that the switch is sitting flush and square to the board. If the switch is sitting flush, move to the next step.

If the switch is not sitting flush, you can reheat the soldered joint to melt the solder and realign the switch as needed.

Step A-07: Solder the remaining switch leads
Once the switch is aligned properly, solder the remaining two leads to the main PCB.

## MAKER GUIDE

Files available at https://github.com/makersmakingchange/Chatterbox | Page 28 of 103

Step A-08: Insert the “Level” switch
Insert one of the two three position switches (A05) into the position labeled “LEVEL” on the main PCB.

Step A-09: Solder one switch lead and check alignment
Solder one of the four leads of the three position slide switch to the main board. Double check that the switch is sitting flush and square to the board. If the switch is sitting flush, move to the next step.

If the switch is not sitting flush, you can reheat the soldered joint to melt the solder and realign the switch as needed.

## MAKER GUIDE

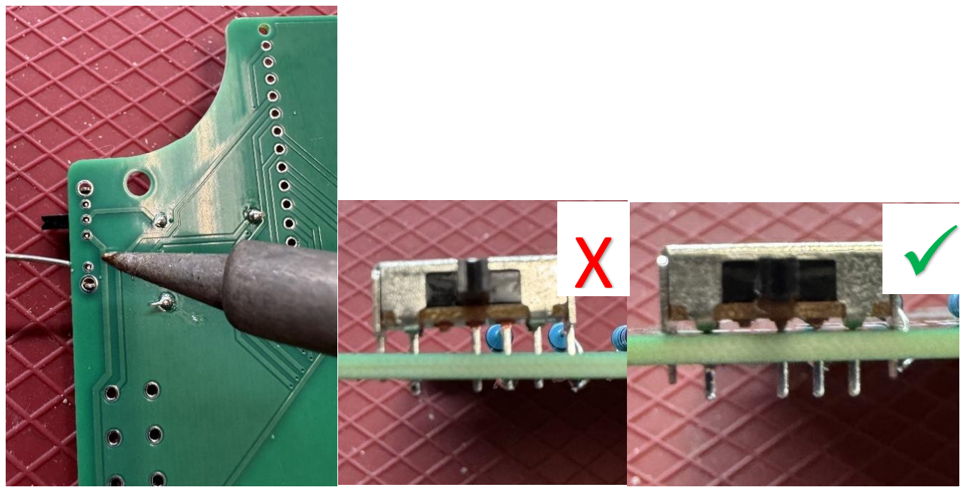
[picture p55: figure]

Files available at https://github.com/makersmakingchange/Chatterbox | Page 29 of 103

Step A-10: Solder the remaining switch leads
Once the switch is aligned properly, solder the remaining three leads to the main PCB.

Step A-11: Insert the “Speed” switch
Insert the remaining three position switches (A05) into the position labeled “SPEED” on the main PCB.

## MAKER GUIDE

Files available at https://github.com/makersmakingchange/Chatterbox | Page 30 of 103

Step A-12: Solder one switch lead and check alignment
Solder one of the four leads of the three position slide switch to the main board. Double check that the switch is sitting flush and square to the board. If the switch is sitting flush, move to the next step.

If the switch is not sitting flush, you can reheat the soldered joint to melt the solder and realign the switch as needed.

Step A-13: Solder the remaining switch leads
Once the switch is aligned properly, solder the remaining three leads to the main PCB.

## MAKER GUIDE

Files available at https://github.com/makersmakingchange/Chatterbox | Page 31 of 103

Step A-14: Insert 8 position female header
Insert the 8 position female header (A06) into the position labeled “SD_CARD_READER” on the main PCB.

Step A-15: Solder one lead on the headers and check alignment
Solder one of the 8 leads to the main PCB. Double check that the headers are sitting flush and square to the board. If the headers are sitting flush, move to the next step.

## MAKER GUIDE

Files available at https://github.com/makersmakingchange/Chatterbox | Page 32 of 103

If the headers are not sitting flush, you can reheat the soldered joint to melt the solder and realign the headers as needed.

Step A-16: Solder the remaining leads
Once the headers are aligned properly, solder the remaining seven leads on the female header to the PCB.

Step A-17: Attach female headers to microcontroller
Attach the 15 position female headers (A07) to the microcontroller (A10).

## MAKER GUIDE

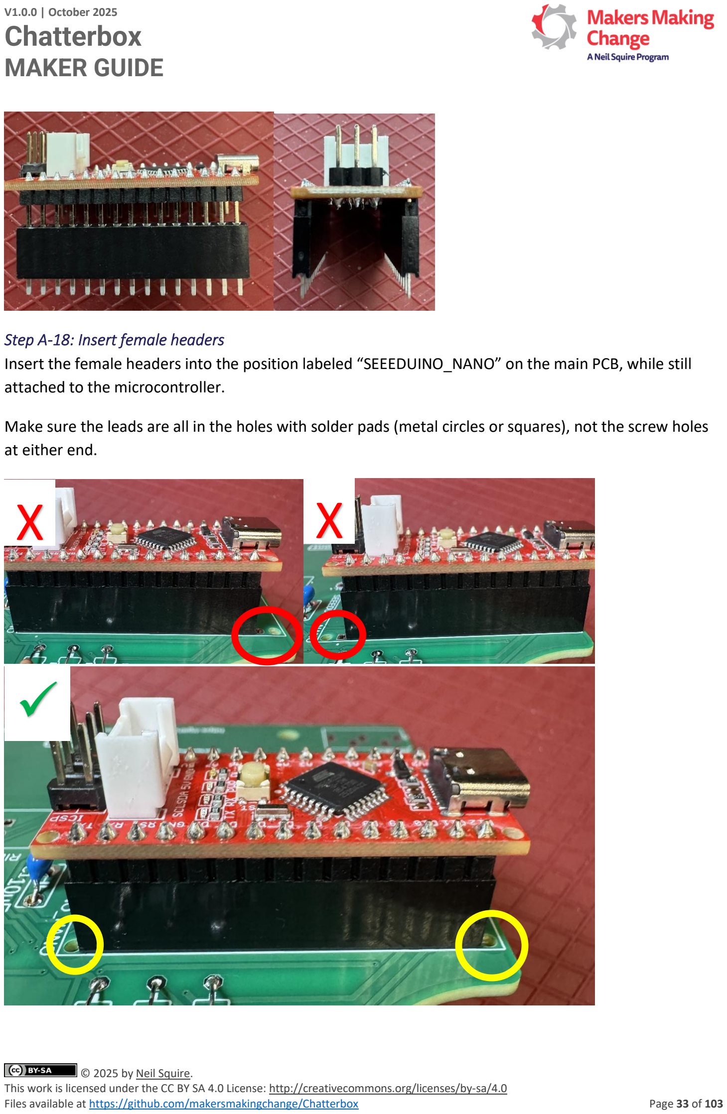
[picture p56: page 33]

Files available at https://github.com/makersmakingchange/Chatterbox | Page 33 of 103

Step A-18: Insert female headers
Insert the female headers into the position labeled “SEEEDUINO_NANO” on the main PCB, while still attached to the microcontroller.

Make sure the leads are all in the holes with solder pads (metal circles or squares), not the screw holes at either end.
X | X

✓

## MAKER GUIDE

Files available at https://github.com/makersmakingchange/Chatterbox | Page 34 of 103

Step A-19: Solder one lead of the female headers and check alignment
Solder one of the 30 leads to the main PCB. Double check that the headers are sitting flush and square to the board. If the headers are sitting flush, move to the next step.

If the headers are not sitting flush, you can reheat the soldered joint to melt the solder and realign the headers as needed.

Step A-20: Solder remaining leads and remove microcontroller
Once the headers are aligned properly, solder the remaining 29 leads on the female headers to the PCB. Once fully soldered, remove the microcontroller from the leads.

Step A-21: Insert the “Next” jack
Insert one of the two mono jacks (A08) into the position labeled “NEXT” on the main PCB.

## MAKER GUIDE

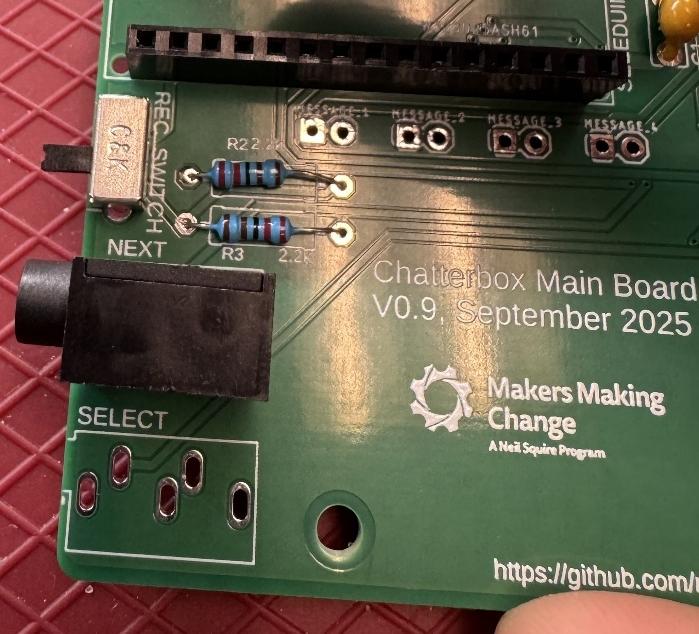
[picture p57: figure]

Files available at https://github.com/makersmakingchange/Chatterbox | Page 35 of 103

Step A-22: Solder one lead of the jack and check alignment
Solder one of the four leads to the main PCB. Double check that the jack is sitting flush and square to the board. If the jack sitting flush, move to the next step.

If the jack is not sitting flush, you can reheat the soldered joint to melt the solder and realign the jack as needed.

Step A-23: Solder remaining leads
Once the jack is aligned properly, solder the remaining three leads to the main PCB.

## MAKER GUIDE

Files available at https://github.com/makersmakingchange/Chatterbox | Page 36 of 103

Step A-24: Insert the “Select” jack
Insert remaining mono jack (A08) into the position labeled “SELECT” on the main PCB.

Step A-25: Solder one lead of the jack and check alignment
Solder one of the four leads to the main PCB. Double check that the jack is sitting flush and square to the board. If the jack sitting flush, move to the next step.

If the jack is not sitting flush, you can reheat the soldered joint to melt the solder and realign the jack as needed.

## MAKER GUIDE

Files available at https://github.com/makersmakingchange/Chatterbox | Page 37 of 103

Step A-26: Solder remaining leads
Once the jack is aligned properly, solder the remaining three leads to the main PCB.

Step A-27: Insert ribbon cable connector
Insert the ribbon cable connector (A09) into the position labeled “RIBBON_CONNECTOR” on the main PCB. Make sure the slot in the top of the connector is on the same side as the opening on the outline on the PCB.

## MAKER GUIDE

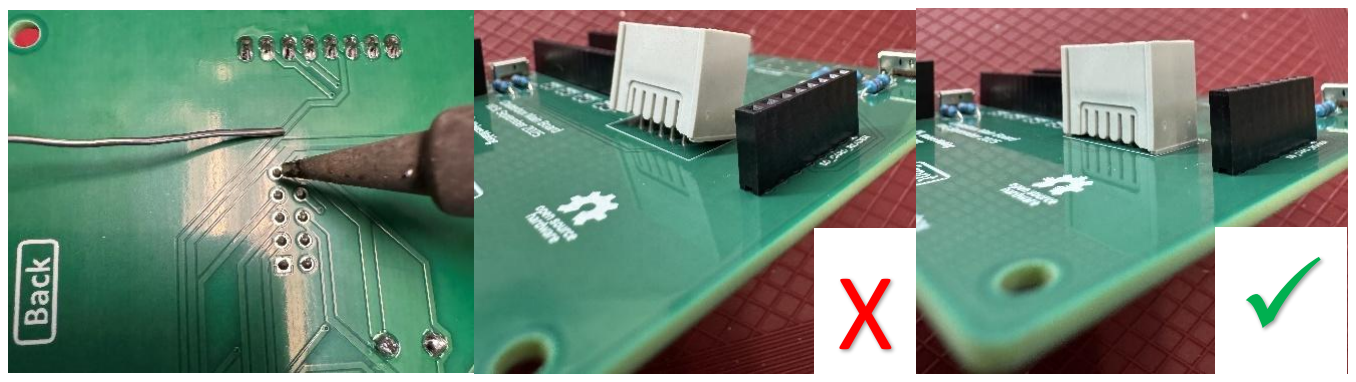
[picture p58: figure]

Files available at https://github.com/makersmakingchange/Chatterbox | Page 38 of 103

Step A-28: Solder one lead and check alignment
Solder one of the 10 leads to the main PCB. Double check that the connector is sitting flush and square to the board. If the connector is sitting flush, move to the next step.

If the connector is not sitting flush, you can reheat the soldered joint to melt the solder and realign the connector as needed.

Step A-29: Solder remaining leads
Once the connector is aligned properly, solder the remaining nine leads to the main PCB.

## MAKER GUIDE

Files available at https://github.com/makersmakingchange/Chatterbox | Page 39 of 103

Step A-30: Insert potentiometer
Insert the potentiometer (A14) into the position labeled “VOLUME” on the main PCB. Make sure the adjustment knob of the potentiometer is pointing out of the PCB.

Step A-31: Solder one lead and check alignment
Solder one of the six leads to the main PCB. Double check that the potentiometer is sitting flush and square to the board. If the potentiometer is sitting flush, move to the next step.

If the potentiometer is not sitting flush, you can reheat the soldered joint to melt the solder and realign the potentiometer as needed.

## MAKER GUIDE

X

Files available at https://github.com/makersmakingchange/Chatterbox | Page 40 of 103

Step A-32: Solder remaining leads
Once the potentiometer is aligned properly, solder the remaining five leads to the main PCB.

✓

## MAKER GUIDE

Files available at https://github.com/makersmakingchange/Chatterbox | Page 41 of 103

Step A-33: Cut wire to length
Cut the 24 AWG wire (A13) into two sections each of the following lengths: 13, 17, 24, and 29 cm. You will have cut off eight pieces of wire from the main length.

Step A-34: Strip ends of wires
Use the wire strippers to strip 0.5 cm of the insulation off both ends of each wire section you cut in Step A-33.

Step A-35: Insert message 1 wires
Insert both of the shortest wires (13 cm) into the positions labeled “MESSAGE_1” on the main PCB. Bend the wires to hold them in place. Make sure the exposed ends of the wires are not touching each other.

## MAKER GUIDE

Files available at https://github.com/makersmakingchange/Chatterbox | Page 42 of 103

Step A-36: Solder the wires and trim excess
Solder the wires to the main PCB. Trim the excess from the wires with the flush cutters.

Step A-37: Insert message 2 wires
Insert both of the next shortest wires (17 cm) into the positions labeled “MESSAGE_2” on the main PCB. Bend the wires to hold them in place. Make sure the exposed ends of the wires are not touching each other.

Step A-38: Solder the wires and trim excess
Solder the wires to the main PCB. Trim the excess from the wires with the flush cutters.

## MAKER GUIDE

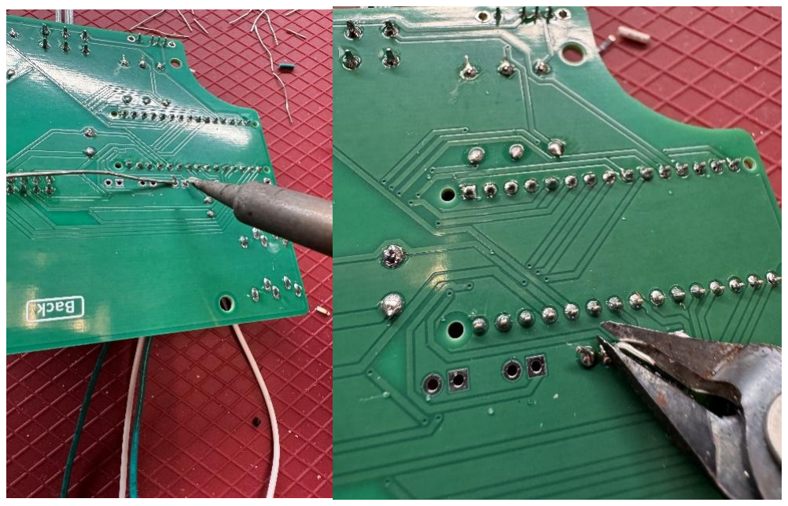
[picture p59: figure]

Files available at https://github.com/makersmakingchange/Chatterbox | Page 43 of 103

Step A-39: Insert message 3 wires
Insert both of the next shortest wires (24 cm) into the positions labeled “MESSAGE_3” on the main PCB. Bend the wires to hold them in place. Make sure the exposed ends of the wires are not touching each other.

Step A-40: Solder the wires and trim excess
Solder the wires to the main PCB. Trim the excess from the wires with the flush cutters.

## MAKER GUIDE

Files available at https://github.com/makersmakingchange/Chatterbox | Page 44 of 103

Step A-41: Insert message 4 wires
Insert both of the last wires (27 cm) into the positions labeled “MESSAGE_4” on the main PCB. Bend the wires to hold them in place. Make sure the exposed ends of the wires are not touching each other.

Step A-42: Solder the wires and trim excess
Solder the wires to the main PCB. Trim the excess from the wires with the flush cutters.

## MAKER GUIDE

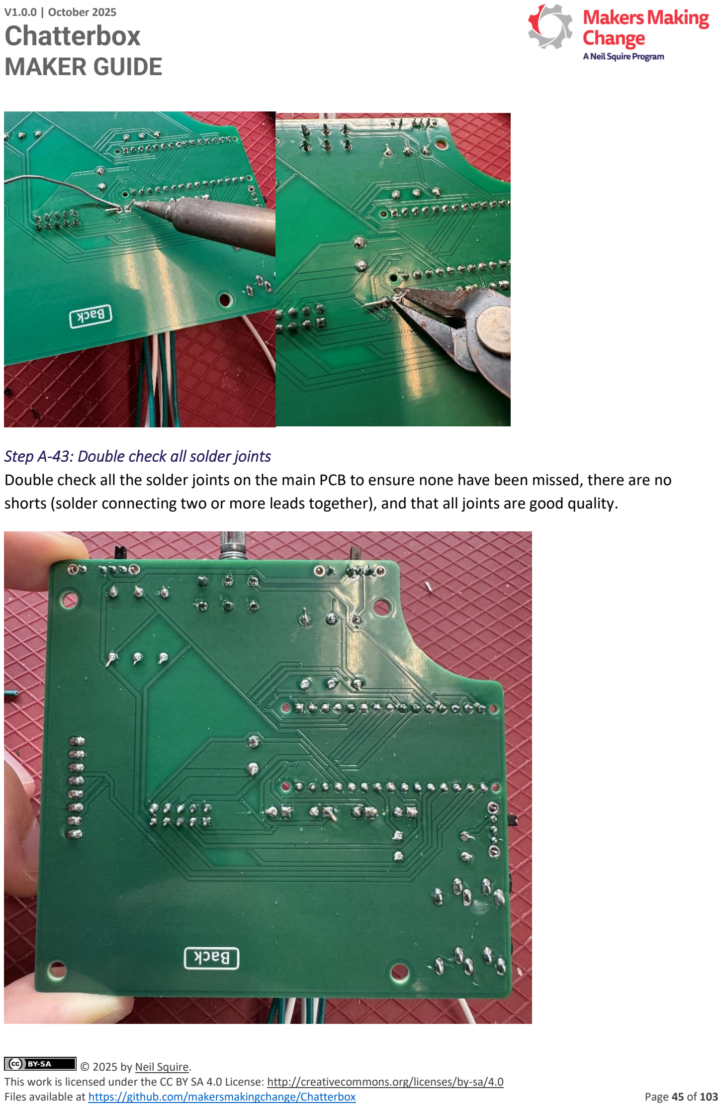
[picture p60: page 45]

Files available at https://github.com/makersmakingchange/Chatterbox | Page 45 of 103

Step A-43: Double check all solder joints
Double check all the solder joints on the main PCB to ensure none have been missed, there are no shorts (solder connecting two or more leads together), and that all joints are good quality.

## MAKER GUIDE

Files available at https://github.com/makersmakingchange/Chatterbox | Page 46 of 103

Step A-44: Solder headers to SD Card Reader
Solder the male header that came with the microSD card reader (A11) to the reader with the short pins of the header in the microSD card reader and the long side of the pins facing away from the reader as shown in the below picture. Insert the microSD card (18) into the reader. You may need to trim one pin from the header that comes with the reader to get it to the correct number of pins.

Step A-45: Insert SD card into reader
Insert the micro SD card (A12) into the slot in the micro SD card reader.

## MAKER GUIDE

X | ✓

Files available at https://github.com/makersmakingchange/Chatterbox | Page 47 of 103

Step A-46: Insert SD card reader into Main PCB
Insert the SD card reader into the female headers labeled “SD_CARD_READER” on the Main PCB. Make sure the reader points off the board and does not block the Ribbon Cable Connector.

Step A-47: Insert Seeeduino Nano into female headers
Insert the Seeeduino Nano (A10) into the female headers on the Main PCB. Make sure the USB-C connector is facing out from the Main PCB.

The Main PCB is now complete.

X | ✓

## MAKER GUIDE

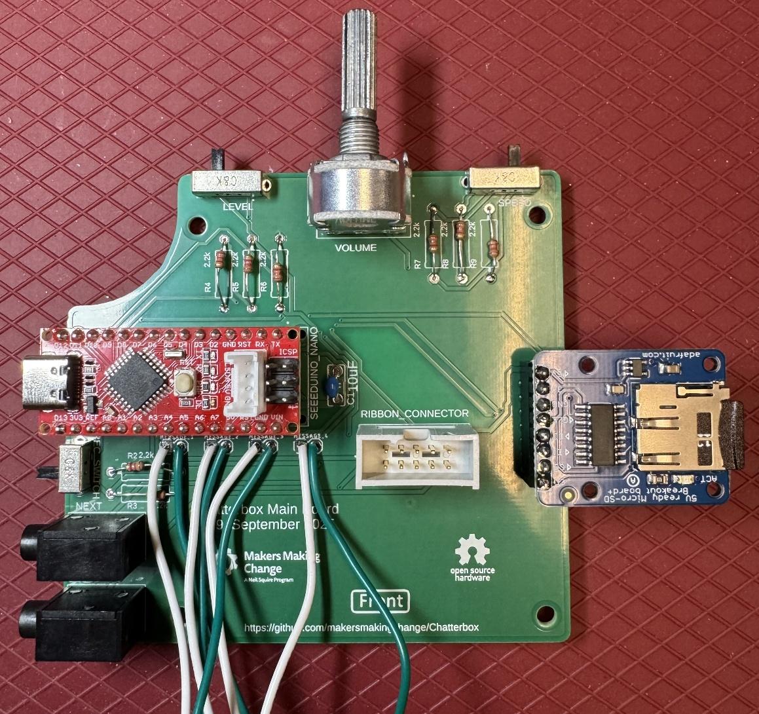
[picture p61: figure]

Files available at https://github.com/makersmakingchange/Chatterbox | Page 48 of 103

### Part B: Secondary PCB

Part B: Required Components Secondary PCB
B01 Secondary
PCB
QTY: 1 | B02 | 10uF
Capacitor
QTY: 2 | B03 | Two
position
switch

QTY: 1

## MAKER GUIDE

Files available at https://github.com/makersmakingchange/Chatterbox | Page 49 of 103
| Note: The capacitor may be labelled with 106, 10u, or the colour may be different.
B04 | 5 position female header | QTY: 2 | B05 | 9V battery clip | QTY: 1 | B06 | Ribbon cable connector | QTY: 1
B07 | Amp | QTY: 1 | B08 | Microphone | QTY: 1 | B09 | 24 AWG wire

QTY:
132
cm
B10 | Speaker | QTY: 1

## MAKER GUIDE

Files available at https://github.com/makersmakingchange/Chatterbox | Page 50 of 103

Part B: Required Tools and Supplies
- Soldering iron
- Solder
- Flush cutters
- Wire strippers
- Precision flathead screw driver (2.5mm or smaller)

Part B: Required Personal Protective Equipment (PPE)
- Safety glasses/goggles

Part B: Secondary PCB Assembly Steps
Note that different components will need to be soldered on different sides of the board. Each step will say from which side of the board (front or back) the part should be inserted.

Step B -00: Break off LED PCBs
Separate the four LED PCBs from the secondary PCB along the mouse bites (small holes). Separate the four LED PCBs from each other along the other mouse bites. In future, the LED PCBs will be separate so we will be able to remove this step.

## MAKER GUIDE

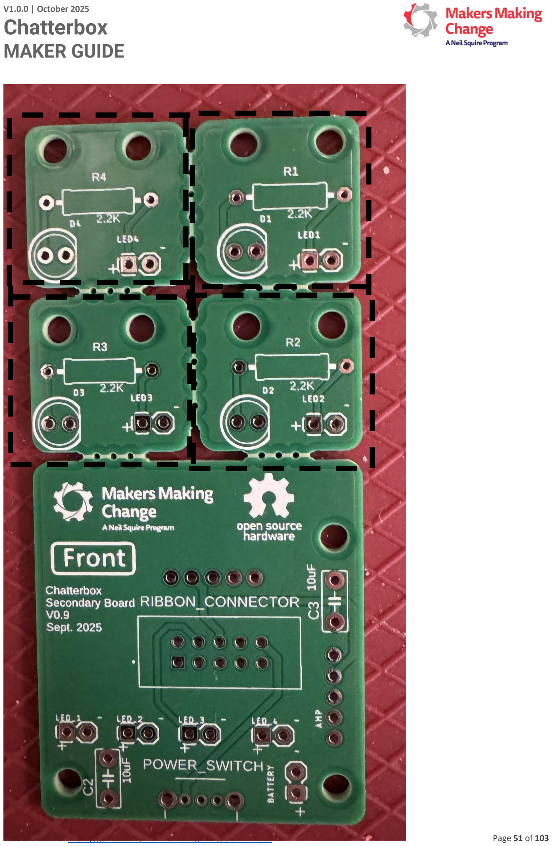
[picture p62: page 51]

Files available at https://github.com/makersmakingchange/Chatterbox | Page 51 of 103

## MAKER GUIDE

Files available at https://github.com/makersmakingchange/Chatterbox | Page 52 of 103

Step B -01: Insert capacitors
Insert the capacitors (B02) into the positions labeled “C_2” and “C_3” from the Front side of the secondary PCB (B01). Bend the leads on the Back side of the board to hold them in place.

Step B -02: Solder capacitor and trim leads
Solder both leads of the capacitor to the pads on the main PCB. Once soldered, trim the excess lead with the flush cutters.

Step B -03: Insert “Power” switch
Insert the two position slide switch (B03) from the Front side of the board into the position labeled “POWER_SWITCH”. Make sure the slider on the switch (the black rectangle) is facing out of the board.

## MAKER GUIDE

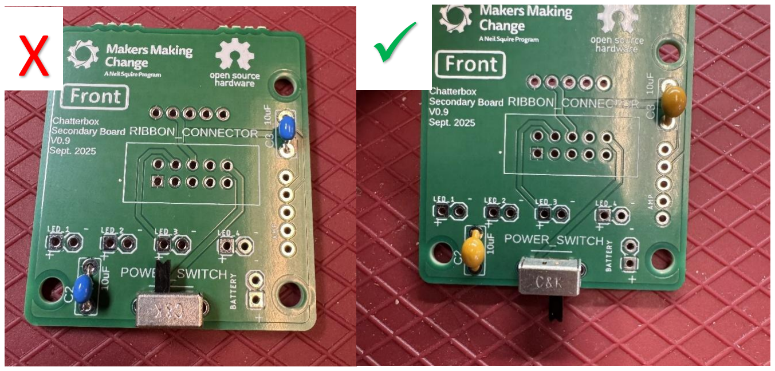
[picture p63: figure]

Files available at https://github.com/makersmakingchange/Chatterbox | Page 53 of 103

Step B -04: Solder one switch lead and check alignment
Solder one of the three leads of the two position slide switch to the main board. Double check that the switch is sitting flush and square to the board. If the switch is sitting flush, move to the next step.

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

Step B -02: Solder the remaining switch leads
Once the switch is aligned properly, solder the remaining two leads to the PCB.

## MAKER GUIDE

Files available at https://github.com/makersmakingchange/Chatterbox | Page 54 of 103

Step B -05: Insert battery cap wires
Insert the wires from the battery cap (B09) into the position labeled “BATTERY” from the Front side of the PCB. Make sure the exposed wires are not touching each other.

NOTE: It is critical that the red wire goes to the positive terminal (labeled with a “+”) and the black wire goes to the negative terminal (labeled with a “-“).

Step B -06: Solder and trim the battery cap wires
Solder the wires from the battery cap to the PCB. Make sure the exposed sections of the wires are not touching. Trim the excess wire after soldering.

## MAKER GUIDE

Files available at https://github.com/makersmakingchange/Chatterbox | Page 55 of 103

Step B -07: Insert amp female headers
Insert one of the two sets of five position female headers (B04) into the position labeled “AMP” from the Front side of the PCB.

Step B -08: Solder one lead of the female headers and check alignment
Solder one of the five leads to the PCB. Double check that the headers are sitting flush and square to the board. If the headers are sitting flush, move to the next step.

If the headers are not sitting flush, you can reheat the soldered joint to melt the solder and realign the headers as needed.

## MAKER GUIDE

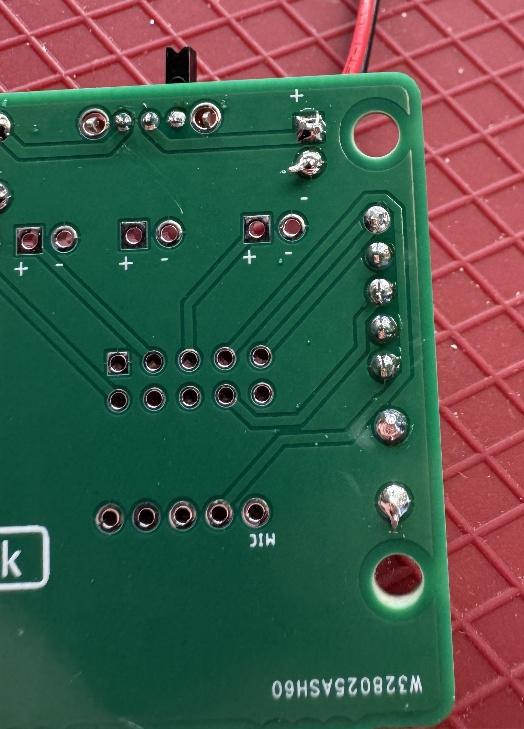
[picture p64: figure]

Files available at https://github.com/makersmakingchange/Chatterbox | Page 56 of 103

Step B -09: Solder the remaining leads
Once the headers are aligned properly, solder the remaining four leads on the female header to the PCB.

Step B -10: Insert ribbon cable connector
Insert the ribbon cable connector (B06) into the position labeled “RIBBON_CONNECTOR” from the Front side of the board. Make sure the slot in the top of the connector is on the same side as the opening in the outline on the PCB.

## MAKER GUIDE

X | ✓

Files available at https://github.com/makersmakingchange/Chatterbox | Page 57 of 103

Step B -11: Solder one lead and check alignment
Solder one of the 10 leads to the PCB. Double check that the connector is sitting flush and square to the board. If the connector is sitting flush, move to the next step.

If the connector is not sitting flush, you can reheat the soldered joint to melt the solder and realign the connector as needed.
X

✓

## MAKER GUIDE

Files available at https://github.com/makersmakingchange/Chatterbox | Page 58 of 103

Step B -12: Solder the remaining leads
Once the connector is aligned properly, solder the remaining nine leads to the PCB.

Step B -13: Cut wires to length
Cut the 24 AWG wire (B09) into two sections each of the following lengths: 8, 14, 19, and 25 cm. You will have cut off eight pieces of wire from the main length.

Step B -14: Strip ends of wires
Use the wire strippers to strip 0.5 cm of the insulation off both ends of each wire section you cut in Step B-07.

## MAKER GUIDE

Files available at https://github.com/makersmakingchange/Chatterbox | Page 59 of 103

Step B -15: Insert LED 1 wires
Insert the shortest wires (8 cm) into the position labeled “LED_1” from the Front of the PCB. Make sure the exposed ends of the wires are not touching.

Step B -16: Solder the wires and trim excess
Solder the wires to the PCB. Trim the excess from the wires with the flush cutters.

Step B -17: Insert LED 2 wires
Insert the next shortest wires (14 cm) into the position labeled “LED_2” from the Front of the PCB. Make sure the exposed ends of the wires are not touching.

## MAKER GUIDE

Files available at https://github.com/makersmakingchange/Chatterbox | Page 60 of 103

Step B -18: Solder the wires and trim excess
Solder the wires to the PCB. Trim the excess from the wires with the flush cutters.

Step B -19: Insert LED 3 wires
Insert the next shortest wires (19 cm) into the position labeled “LED_3” from the Front of the PCB. Make sure the exposed ends of the wires are not touching.

## MAKER GUIDE

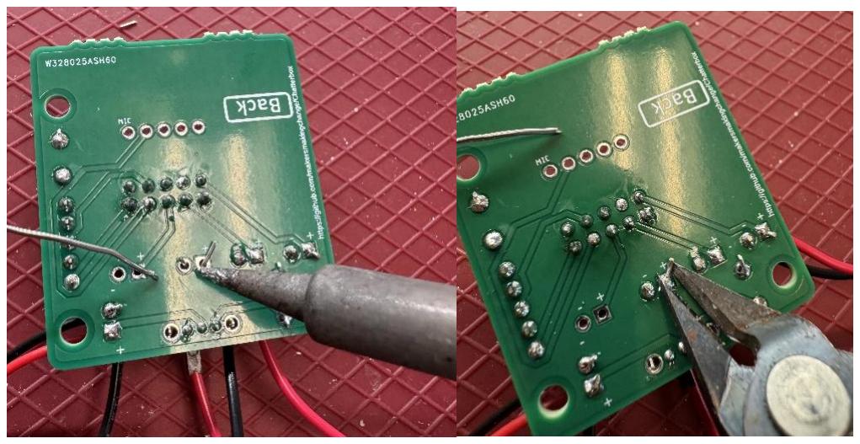
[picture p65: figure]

Files available at https://github.com/makersmakingchange/Chatterbox | Page 61 of 103

Step B -20: Solder the wires and trim excess
Solder the wires to the PCB. Trim the excess from the wires with the flush cutters.

Step B -21: Insert LED 4 wires
Insert the next longest wires (24 cm) into the position labeled “LED_4” from the Front of the PCB. Make sure the exposed ends of the wires are not touching.

## MAKER GUIDE

Files available at https://github.com/makersmakingchange/Chatterbox | Page 62 of 103

Step B -22: Solder the wires and trim excess
Solder the wires to the PCB. Trim the excess from the wires with the flush cutters.

Step B -23: Insert microphone female headers
Insert the remaining set of five position female headers (B04) into the position labeled “MIC” from the Back side of the PCB.

## MAKER GUIDE

Files available at https://github.com/makersmakingchange/Chatterbox | Page 63 of 103

Step B -24: Solder one lead of the female headers and check alignment
Solder one of the five leads to the PCB. Double check that the headers are sitting flush and square to the board. If the headers are sitting flush, move to the next step.

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

## MAKER GUIDE

Files available at https://github.com/makersmakingchange/Chatterbox | Page 64 of 103

Step B -25: Solder the remaining leads
Once the headers are aligned properly, solder the remaining four leads on the female header to the PCB.

Step B -26: Solder male headers to microphone
Insert the shorter side of the male headers through the microphone PCB (B08) from the side without the round microphone. Solder the headers so they are flush and square to the microphone PCB.

Step B -27: Insert microphone into female headers
Insert the long end of the male headers from the microphone into the “MIC” female headers on the secondary PCB. Make sure the circular microphone is directed away from the secondary PCB.

## MAKER GUIDE

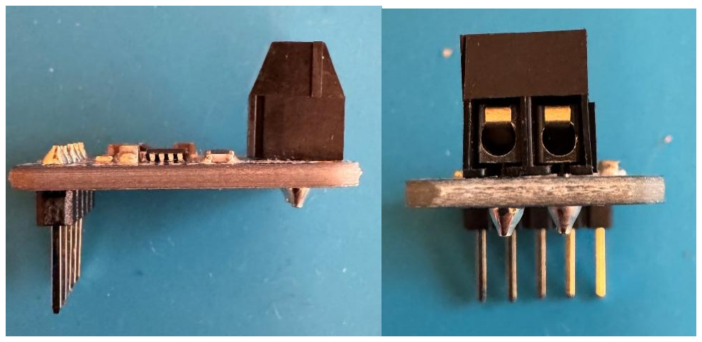
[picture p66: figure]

Files available at https://github.com/makersmakingchange/Chatterbox | Page 65 of 103

Step B -28: Solder male headers to amp
Insert the shorter side of the male headers through the amp PCB (B07) from the side without any electronics on it. Solder the headers so they are flush and square to the microphone board.

Step B -29: Solder screw terminals to amp
Insert the screw terminal into the amp PCB (B07) from the side with the electronics on it. Make sure the screw terminal openings face out from the board. Solder the screw terminals so they are flush and square to the amp PCB.

Step B -30: Trim and strip speaker wires
Trim off the plug terminal from the speaker wires. Strip roughly 0.5 cm of the insulation from the ends of the speaker wires.

## MAKER GUIDE

Files available at https://github.com/makersmakingchange/Chatterbox | Page 66 of 103

Step B -31: Connect speaker to amp
Take the stripped ends of the speaker wire, and screw them into the terminal blocks on the amp using the small flathead screwdriver.

It is critical that the red wire is connected to the terminal labeled with a “+” and the black wire is connected to the terminal labeled with a “-“. You may notice the black wire has some red on it, but the red wire will only have red.

Step B -32: Insert amp into female headers
Insert the long end of the male headers from the amp into the “AMP” female headers on the secondary PCB. Make sure the amp is facing away from the secondary PCB.

## MAKER GUIDE

Files available at https://github.com/makersmakingchange/Chatterbox | Page 67 of 103

Step B -33: Double check all solder connections
Double check all the solder joints on the secondary PCB to ensure none have been missed, there are no shorts (solder connecting two or more leads together), and that all joints are good quality.

The secondary PCB is now complete.

## MAKER GUIDE

Files available at https://github.com/makersmakingchange/Chatterbox | Page 68 of 103

### Part C: LED PCBs

Part C: Required Components
LED PCBs
C01 | LED PCB | QTY: 4 | C02 | 2.2k Ohm resistor | QTY: 4 | C03 | 5mm LED | QTY: 4
| | | Note: The resistor body colour may change, but the bands will be the same.
C04 | Completed Secondary PCB | QTY: 1

## MAKER GUIDE

Files available at https://github.com/makersmakingchange/Chatterbox | Page 69 of 103

Part C: Required Tools and Supplies
- Soldering iron
- Solder
- Flush cutters

Part C: Required Personal Protective Equipment (PPE)
- Safety glasses/goggles

Part C: LED PCB Assembly Steps

Step C-00: Sort LED PCBs
Currently, the are four LED PCBs have slight differences which mean they must be connected to their corresponding number on the Secondary PCB (i.e. LED 1 to LED 1). Start with LED 1, and work up to LED 4, making sure when you connect the correct boards on Step C-06. In future, the four boards will be identical, so we can remove this step.

Step C -01: Insert resistor
Insert the resistors (C02) into the spaces “R_1”on the LED PCB (C01). Make sure the resistor is lying flat on the board, and bend the leads to hold the resistor in place.

## MAKER GUIDE

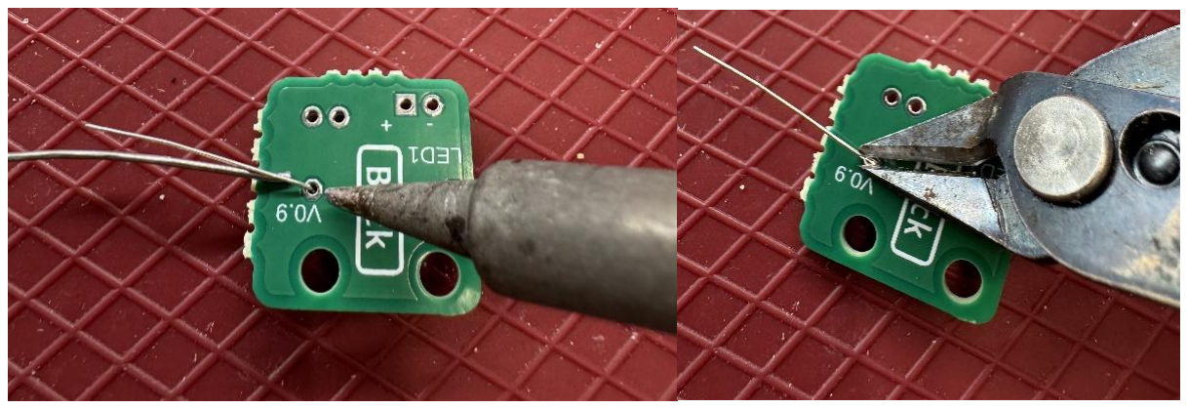
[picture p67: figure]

Files available at https://github.com/makersmakingchange/Chatterbox | Page 70 of 103

Step C -02: Solder and trim resistor leads
Solder both leads of the resistor to the PCB. Once the leads are soldered, trim the excess wire off using the flush cutters.

Step C -03: Insert the LED
Insert the LED (C03) into the position labeled “D1”. It is critical that the LED is oriented properly. There are two ways to check the orientation: a flat section on the LED, and the length of the leads. The flat section on the LED should line up with the flat side on the outline of the LED on the PCB. The leads are different lengths, and the longer lead should be closest to the edge of the PCB.

## MAKER GUIDE

Files available at https://github.com/makersmakingchange/Chatterbox | Page 71 of 103

Step C -04: Solder one lead and check alignment
Solder one of the two leads to the PCB. Double check that the LED is sitting flush and square to the board. If the LED is sitting flush, move to the next step.

If the LED is not sitting flush, you can reheat the soldered joint to melt the solder and realign the LED as needed.

## MAKER GUIDE

Files available at https://github.com/makersmakingchange/Chatterbox | Page 72 of 103

Step C -05: Solder the remaining lead and trim excess
Once the LED is aligned properly, solder the remaining lead to the PCB. Trim the excess from both leads.

Step C -06: Connect LED PCB to the Secondary PCB
Connect the wires from the Secondary PCB (C04) to the LED PCB. It is critical that the polarity (positive and negative) of the wires is the same on LED PCB as it is on the Secondary PCB. Make sure the wire coming from the position labeled “+” on the Secondary PCB goes to the “+” on the LED PCB, and the “-“ goes to the “-“.

## MAKER GUIDE

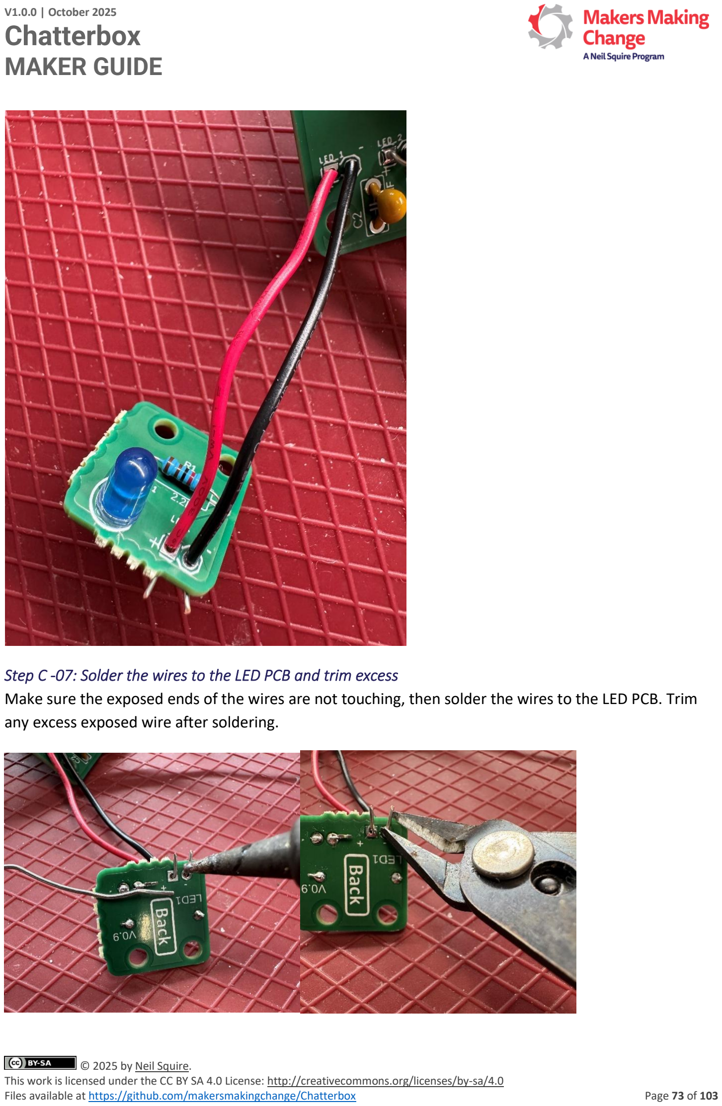
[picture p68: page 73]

Files available at https://github.com/makersmakingchange/Chatterbox | Page 73 of 103

Step C -07: Solder the wires to the LED PCB and trim excess
Make sure the exposed ends of the wires are not touching, then solder the wires to the LED PCB. Trim any excess exposed wire after soldering.

## MAKER GUIDE

Files available at https://github.com/makersmakingchange/Chatterbox | Page 74 of 103

Step C -08: Double check all solder connections
Double check all the solder joints on the LED PCB to ensure none have been missed, there are no shorts (solder connecting two or more leads together), and that all joints are good quality.

Step C -09: Repeat Steps C-01 to C-08 for the remaining three LED PCBs
Repeat Steps C-01 to C-08 for the remaining three LED PCBs. By the end, all the wires from the Secondary PCB should be connected to LED PCBs.

Once all LED PCBs have been connected to the Secondary PCB, this section is complete.

## MAKER GUIDE

Files available at https://github.com/makersmakingchange/Chatterbox | Page 75 of 103

### Part D: Enclosure Assembly

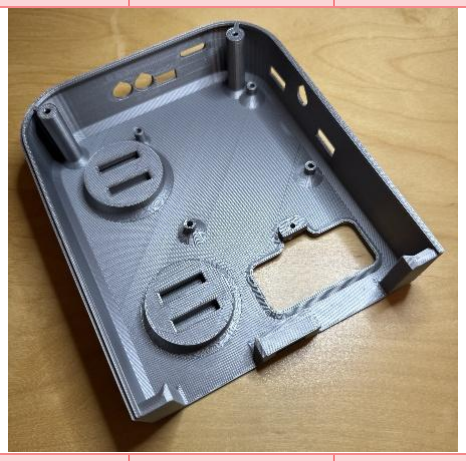
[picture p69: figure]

Part D: Required Components Enclosure
D01 Enclosure
Bottom -
Left
QTY: 1 | D02 | Enclosure
Bottom -
Right
QTY: 1 | D03 | Assembled
Main PCB

QTY: 1

D03 #4x3/8”
machine
screw
QTY: 20 | D04 | Centre
support
QTY: 2 | D05 | Button base | QTY: 4
D07 | Tactile
switch
QTY: 4 | D08 | Enclosure
Top - Left
QTY: 1 | D09 | Enclosure
Top - Right

QTY: 1

## MAKER GUIDE

Files available at https://github.com/makersmakingchange/Chatterbox | Page 76 of 103
D10 | Ribbon
Cable
QTY: 1 | D11 | Assembled
Secondary
PCB and LED
PCBs
QTY: 4 | D12 | Button
insert

QTY: 4

D13 | Button cap | QTY: 4 | D14 | Label holder | QTY: 4 | D15 | 9V battery | QTY: 1
D16 | Battery
Cover
QTY: 1 | D17 | Volume
knob
QTY: 1 | D18 | Slide Switch
Cover

QTY: 4

## MAKER GUIDE

Files available at https://github.com/makersmakingchange/Chatterbox | Page 77 of 103
D19 | Slide Switch Cover Pin

QTY: 4

Part D: Required Tools and Supplies
- Phillips head screwdriver (#2)
- Flush cutters
- Soldering iron
- Solder
- Hot glue gun and glue/Super glue

Part D: Required Personal Protective Equipment (PPE)
- Safety glasses/goggles

Part D: Enclosure Assembly Steps

Step D -01: Trim switch leads
Use a flush cutter to trim off the leads on one side of each of the tactile switches (D07). Make sure the leads are cut flush against the side of the switch and do not extend below the bottom of the switch.

## MAKER GUIDE

Files available at https://github.com/makersmakingchange/Chatterbox | Page 78 of 103

Step D -02: Straighten remaining switch leads
Straighten the remaining switch leads, ensuring they stick straight out from the side of the switches.

Step D -03: Trim mounting lugs
Use the flush cutters to trim the plastic mounting lugs (the plastic cylinders) off the bottom of the switches. Make sure the lugs are cut flush, with no remaining bumps.

Step D -04: Solder switches to message wires from Main PCB
Starting with the wires leading from “MESSAGE_1” on the Main PCB (D03), solder one wire from the PCB to one of the leads on one switch. Solder the other wire to the other lead, making sure not to connect the two sides together with touching exposed wire or solder.

## MAKER GUIDE

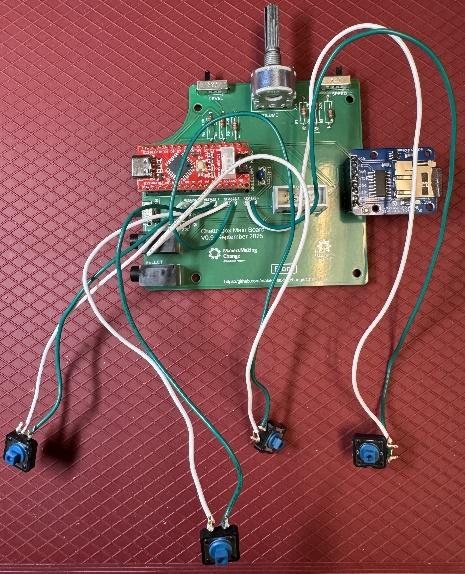
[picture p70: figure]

Files available at https://github.com/makersmakingchange/Chatterbox | Page 79 of 103

Repeat this step for the remaining switches and sets of wires.

Step D -05: Connect bottom parts of the enclosure
Take the Enclosure Bottom – Left (D01) and Enclosure Bottom – Right (D02) and line up the connection snaps in the centre. Keeping your fingers out of the way, push the two parts together firmly, until they snap into place. It may help to angle the pieces while pushing together.

## MAKER GUIDE

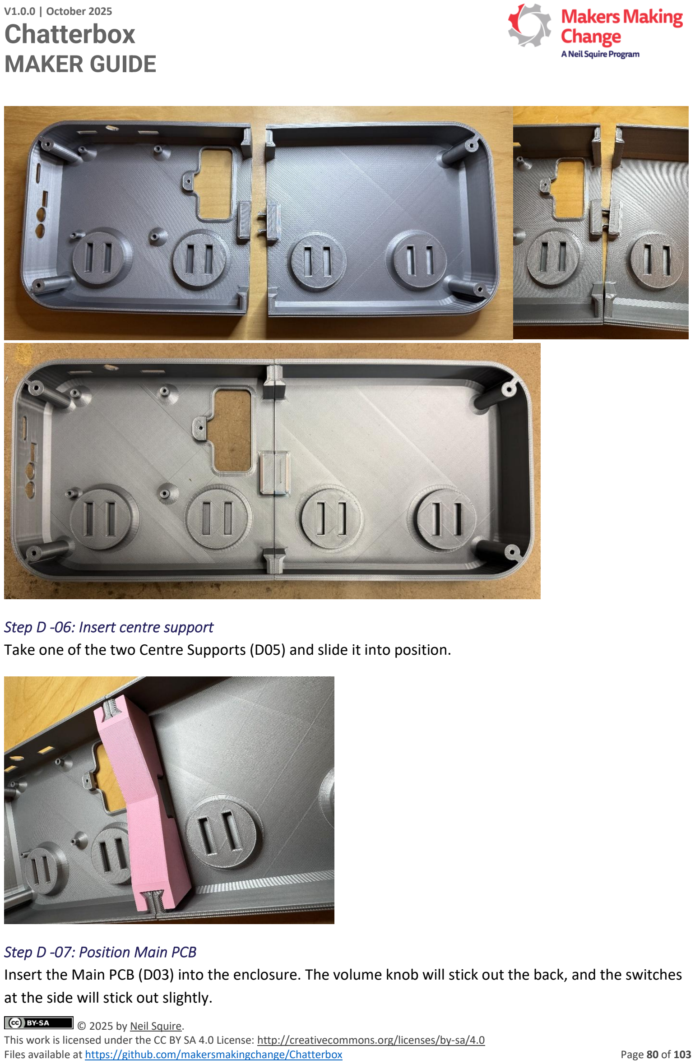
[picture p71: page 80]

Files available at https://github.com/makersmakingchange/Chatterbox | Page 80 of 103

Step D -06: Insert centre support
Take one of the two Centre Supports (D05) and slide it into position.

Step D -07: Position Main PCB
Insert the Main PCB (D03) into the enclosure. The volume knob will stick out the back, and the switches at the side will stick out slightly.

## MAKER GUIDE

Files available at https://github.com/makersmakingchange/Chatterbox | Page 81 of 103

Step D -08: Screw down main PCB
Use four of the #4 screws (D04) to connect the main PCB to the enclosure bottom.

Step D -09: Insert button bases into enclosure
Insert each of the four Button Bases (D06) into the Enclosure Bottom. Make sure the flat side of the bases are closest to the inside of enclosure, and the rounded side is closest to the outside edge. Press the bases firmly until they snap into place.

## MAKER GUIDE

Files available at https://github.com/makersmakingchange/Chatterbox | Page 82 of 103

Step D -10: Glue message switches to bases
Working one switch at a time, glue the switches to their corresponding bases. The messages go from 1 to 4 from left to right (i.e., the switch connected to “MESSAGE_1” on the Main PCB should be in the left-most base, closest to the Main PCB, and the “MESSAGE”4” switch will be on the furthest right base). The wire lengths have been cut to make it so a switch cannot be attached to a base further down from its correct position (ex: the wires from “MESSAGE_1” are too short to reach the second base).

Make sure that the switches are glued flat to the base and are not sitting proud or at an angle.

Step D -11: Bend wires flat to bases
Bend the wires from each switch so they lit flat against the flat side of the button bases.

## MAKER GUIDE

Files available at https://github.com/makersmakingchange/Chatterbox | Page 83 of 103

Step D -12: Connect ribbon cable
Connect the ribbon cable (D10) to the ribbon cable connector on the Main PCB.

## MAKER GUIDE

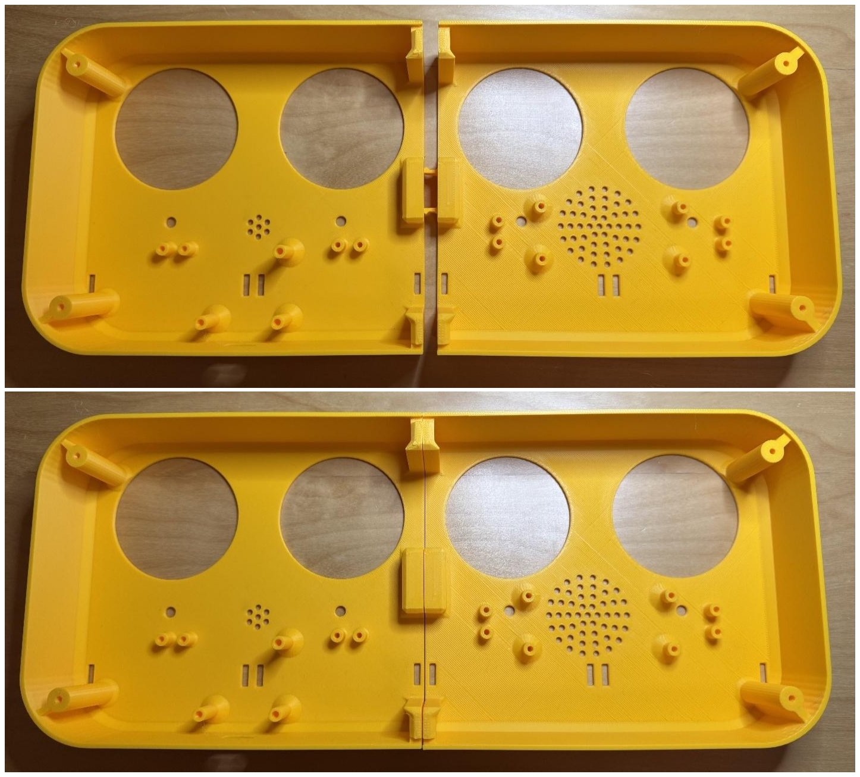
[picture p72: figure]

Files available at https://github.com/makersmakingchange/Chatterbox | Page 84 of 103

Step D -13: Connect top parts of the enclosure
Take the Enclosure Top – Left (D08) and Enclosure Top – Right (D09) and line up the connection snaps in the centre. Keeping your fingers out of the way, push the two parts together firmly, until they snap into place. It may help to angle the pieces while pushing together.

Step D -14: Insert centre support
Take the remaining Centre Support (D05) and slide it into position.

## MAKER GUIDE

Files available at https://github.com/makersmakingchange/Chatterbox | Page 85 of 103

Step D -15: Insert Secondary PCB
Insert the Secondary PCB (D11) into position on the enclosure top. The power switch should stick out from the edge of the enclosure, and the mic should be facing toward the holes in the enclosure top.

Step D -16: Screw down Secondary PCB
Use three of the #4 screws (D04) to fix the Secondary PCB to the enclosure top.

## MAKER GUIDE

Files available at https://github.com/makersmakingchange/Chatterbox | Page 86 of 103

Step D -17: Attach LED PCBs to enclosure top
Working one LED PCB at a time, position the PCBs to the LEDs line up with the holes in the top of the enclosure and the screw holes line up with the posts on the top of the enclosure. Like the message wires, the LED wires are cut to lengths to make it so the PCB will not reach a position too far from its required position.

Once the PCB is aligned correctly, secure it to the enclosure with two of the #4 screws.

Repeat this step for the remaining three LED PCBs.

## MAKER GUIDE

Files available at https://github.com/makersmakingchange/Chatterbox | Page 87 of 103

Step D -18: Connect speaker to enclosure top
Use four of the #4 screws to connect the speaker to the enclosure top. Make sure the speaker faces toward the holes in the top of the enclosure top.

Step D -19: Press slide switch cover onto slide switches
Press a slide switch cover (D18) onto each slide switch from outside of the enclosure. Push the cover until it is flush against the switch.

## MAKER GUIDE

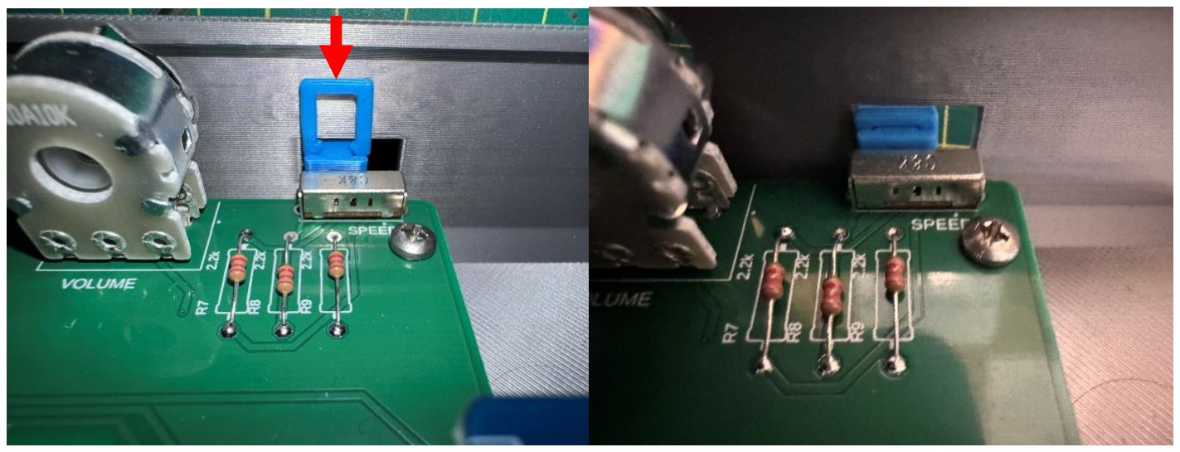
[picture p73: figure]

Files available at https://github.com/makersmakingchange/Chatterbox | Page 88 of 103

Step D -20: Add slide switch cover pin to slide switch covers.
Add the slide switch cover pin (D19) onto each slide switch. To help align it, you can slide the pin along the inside wall of the enclosure before pressing it into place on the slide switch cover.

Step D -21: Connect ribbon cable to Secondary PCB
Plug the ribbon cable into the ribbon cable connector on the Secondary PCB.

NOTE: You may want to move to Part E: Flashing the Firmware to the Chatterbox before completely assembling the enclosure. Some issues you may encounter when flashing the firmware may require you to access the electronics to troubleshoot.

## MAKER GUIDE

Files available at https://github.com/makersmakingchange/Chatterbox | Page 89 of 103

Step D -22: Connect top and bottom halves of the enclosure
Line up the two halves of the enclosures, and fold them together. Use four of the #4 screws to connect the top and bottom halves.

Step D -23: Connect the battery
Connect the 9V battery (D15) to the battery cap.

## MAKER GUIDE

Files available at https://github.com/makersmakingchange/Chatterbox | Page 90 of 103

Step D -24: Insert battery into battery cover
Slide the battery into the battery cover (D16). Make sure the wires from the battery cap face toward the open section.

## MAKER GUIDE

X | ✓

Files available at https://github.com/makersmakingchange/Chatterbox | Page 91 of 103

Step D -25: Connect battery cover to enclosure
Use the remaining #4 screw to connect the battery cover to the enclosure. The screw head should not stick past the bottom of the battery cover.

✓

## MAKER GUIDE

Files available at https://github.com/makersmakingchange/Chatterbox | Page 92 of 103

Step D -26: Put button inserts into button caps
Insert the Button Inserts (D12) into the Button Caps (D13). Line the tabs on the inserts up with the slots on the inside edge of the cap. Press firmly to snap the inserts into place. The insert should slide up and down easily within the cap, but no fall out or rotate.

## MAKER GUIDE

Files available at https://github.com/makersmakingchange/Chatterbox | Page 93 of 103

Repeat this step for the remaining three inserts and caps.

Step D -27: Screw button caps onto bases
Screw the button caps onto the button bases. The caps should stay flat while screwing on (i.e. not tilt to the side) and should screw on smoothly without a lot of resistance. If the cap is going on at a tilt or out encounter a lot of resistance, reposition the cap and try again.

The caps are designed to be able to rotate freely on the bases, so they will continue to spin, even when completely screwed down. To check the cap is fully attached to the base, try pressing on the cap. You

## MAKER GUIDE

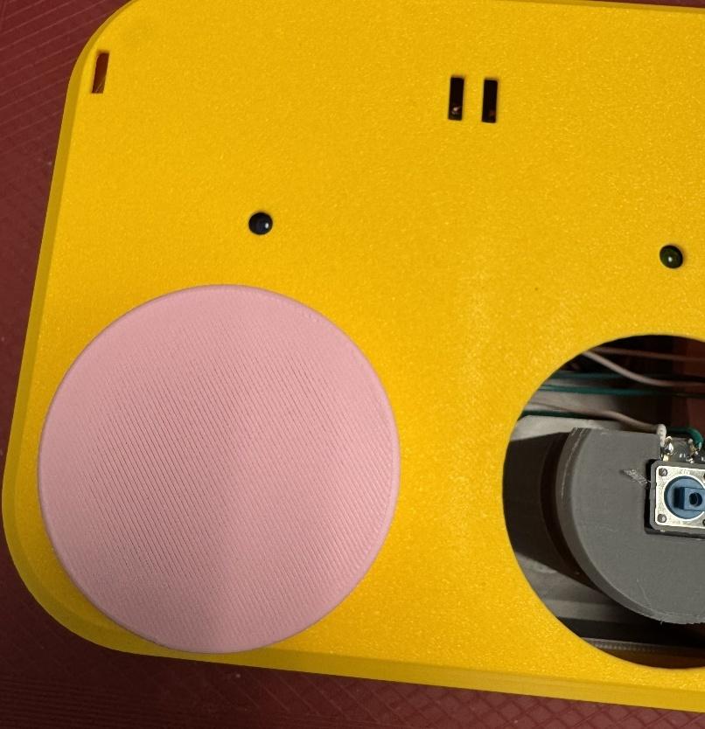
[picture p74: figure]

Files available at https://github.com/makersmakingchange/Chatterbox | Page 94 of 103

should be able to feel and/or hear the tactile switch being pushed. If that is not the case, try unscrewing the cap and screwing it back on.

Repeat this step for the remaining three caps.

Step D -28: Connect label holders (If the requestor asked for them to come connected)
If the requestor asked for the label holders (D14) to be connected, connect the label holders. Line up the holders with the slots in the enclosure. Keeping your fingers out of the way, push firmly to snap the holders in place. It may help to angle the holders when pushing them in.

## MAKER GUIDE

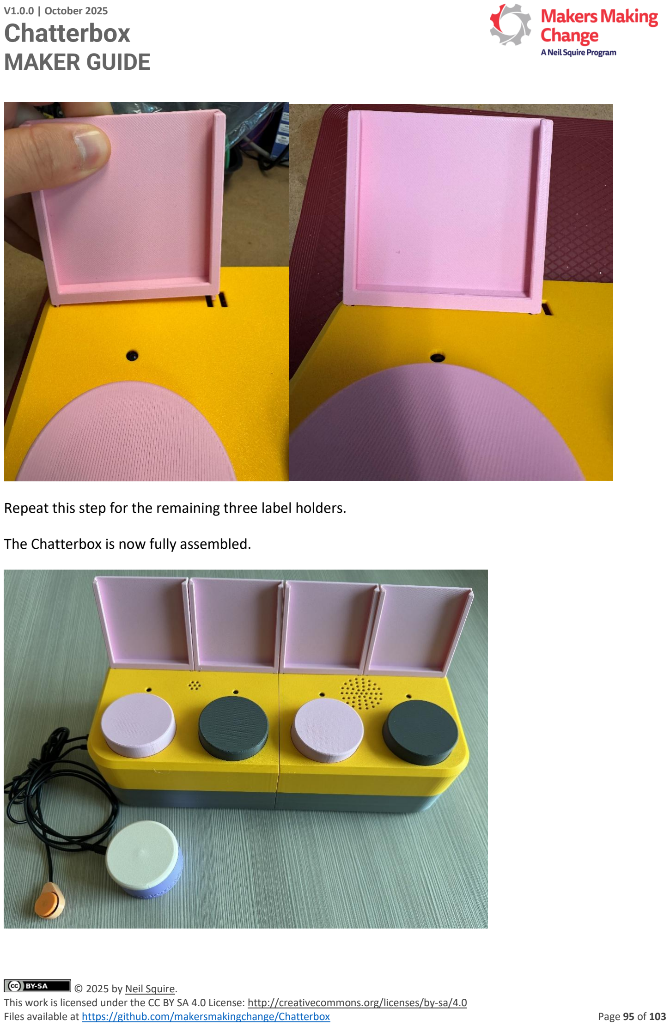
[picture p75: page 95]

Files available at https://github.com/makersmakingchange/Chatterbox | Page 95 of 103

Repeat this step for the remaining three label holders.

The Chatterbox is now fully assembled.

## MAKER GUIDE

Files available at https://github.com/makersmakingchange/Chatterbox | Page 96 of 103

### Part E: Flashing Firmware to the Chatterbox

Part E: Required Components
- Assembled Chatterbox
- USB-C cable
- Computer that can install and run Arduino IDE

Part E: Required Tools and Supplies
- Computer that is able to install Arduino IDE and other Arduino libraries to flash firmware
- USB C cable to plug into the Chatterbox

Step E-01: Connect the Chatterbox to the Computer
Make sure the power switch on the Chatterbox is in the “OFF” position. Plug the USB C cable into the port labeled “USB” on the side of the Chatterbox, and plug the other end of the cable into your computer. The computer will provide power to the Chatterbox, so you can leave the power switch set to “OFF”.

Step E-02: Setup Arduino IDE on Computer
1. Download Arduino IDE for your operating system at https://www.arduino.cc/en/software.
2. Install the Arduino IDE.

Step E-03: Setup Arduino IDE for the Seeeduino Nano
1. Open Arduino IDE.
2. Click on File -> Preferences
3. Locate the text field that reads Additional Boards Manager URLs beside it.
4. Copy and paste the following link into the field as a new line:

raw.githubusercontent.com/Seeed-Studio/Seeed_Platform/master/package_legacy_seeeduino_boards_index.json (https://raw.githubusercontent.com/Seeed-Studio/Seeed_Platform/master/package_legacy_seeeduino_boards_index.json)

## MAKER GUIDE

Files available at https://github.com/makersmakingchange/Chatterbox | Page 97 of 103
5. Click on OK.
6. Restart the Arduino IDE by closing and opening the program.
7. Open the Boards Manager option from the Tools -> Board -> Boards Manager… menu.
8. Search for “Seeeduino AVR” and select “Seeeduino AVR” by Seeed Studio. Make sure you select the exact board manager name stated as there may be some with similar names that will not work.
9. Click Install to install the board.

Step E-04: Install Libraries
1. Go to the Tools -> Manage Libraries… menu.
2. For each library in the table below, search for the name. Ensure the Author and Version is correct, then install the library. If prompted to install any dependent libraries, click OK.
Library Name | Author | Version
TMRpcm | TMRh20 | 1.3.6
StateMachine | Jose Rullan | 1.0.13
Neotimer | Jose Rullan | 1.1.6

Step E-05: Enable Recording
Find the folder where the TMRpcm library was installed. This is usually in C:\Users\[NAME]\sketchbook\libraries\TMRpcm. Open the file pcmConfig.h in notepad or a similar text editor.

## MAKER GUIDE

Files available at https://github.com/makersmakingchange/Chatterbox | Page 98 of 103

Uncomment the line “#define buffSize 128” by removing the “//” before #define buffSize128

Uncomment the line “#define ENABLE_RECORDING” by removing the “//” before #define ENABLE_RECORDING

Save the file and close it.

Step E-06: Setup Local Code Directory
1. Download the Firmware_Files from the GitHub Repository

<Insert link to GitHub firmware files zip file>

2. Extract / unzip the folder to a known location on your computer.
3. Confirm you have the following folder structure:
- Chatterbox_Firmware (folder)
- Chatterbox_Firmware.ino

Step E-07: Flash Firmware to the Chatterbox
1. Open the Chatterbox_Firmware.ino with Arduino IDE.
2. Select Seeeduino Nano from the Tools -> Board -> <Boards Type> menu
3. Connect the Chatterbox to the computer using the USB-C cable.
4. Select the correct port from the Tools -> Port menu.
5. Verify and upload to code by clicking the arrow in the top-left corner of the Arduino program.

### Testing

It is important to test the following functions of the Chatterbox before it is sent to the requestor. If you encounter any issues while testing, refer to the Troubleshooting section for help solving the problem. The tests are summarized in the table below, to make it easy to check if all tests have been completed. Each test is described in detail following the table.

Test | Description | Passed or Failed
Battery power | Check the device powers on from the battery

## MAKER GUIDE

Files available at https://github.com/makersmakingchange/Chatterbox | Page 99 of 103
Mode switch | -Check the mode switch changes modes - Check all LEDs blink while in Record Mode
Record Messages | - Record a message on each button on one level - Check that only the one LED blinks while recording on a switch - Check that the messages play back in Record Mode - Check that playback is audible/clear
Level switch | -Check that moving the Level switch changes the recording/playback level - Record new messages for each button at each level - Check that message play back in Record Mode
Message Playback | - Check that messages play back in Playback mode - Check that only the LED for the message being played lights up
Switch Scanning | - Check that pressing the Select switch once starts switch scanning - Check that the LED for a message stays lit during the delay before playing the next message - Check that only the playing message LED stays lit - Check that switch scanning stops if the last message times out - Check that pressing the Select switch again while switch scanning replays the current message
Next switch | -Check that pressing the Next switch when not switch scanning does nothing - Check that pressing the Next switch while switch scanning moves to the next message
Speed switch | -Check that moving the Speed switch changes the length of the delay between messages being automatically played while switch scanning - Check all three speeds
Volume | -Check that the volume knob changes the volume of the messages

### Battery Power

Slide the Level and Speed switches to the first positions (left-most when looking at them, labeled “1” on the enclosure). Slide the Mode switch to the position closest to the USB port (this is the Record mode position).

With the Chatterbox unplugged from any other power source, turn the power switch to the “On” position. The Chatterbox should turn on. If it’s in Record mode, all four lights will start blinking. If it is in Playback mode, no lights will turn on, but starting switch scanning or pressing a message button should like the LEDs as messages play. Note, no messages will play if they have not been recorded yet.

## MAKER GUIDE

Files available at https://github.com/makersmakingchange/Chatterbox | Page 100 of 103

Passing this test means the device powers on with the battery.

### Mode Switch

With the Chatterbox on, slide the Mode switch to its different positions (only two positions). As you change the mode, the LEDs should either all blink (Recording mode), or no LEDs should light up unless a message is being played.

Passing this test means the Mode switch changes mode consistently.

### Record Messages

With the Chatterbox on and in Recording mode, press and hold one of the message buttons. Once the other LEDs stop blinking and only the LED for the button being held is bringing, start recording the message you would like on that button (ex: say “Level 1, Message 1” for the first button on the first level). Once you have finished the message, release the button. All LEDs should start blinking again after you release the button. Press the button to preview the message; the Chatterbox should play that message back to you.

Record and preview a message on each of the buttons for that message level.

Passing this test means that you can record and preview messages on each of the buttons.

### Level Switch

Move the Level switch to position 2 (the centre position) to switch to Level 2. Repeat the Record Messages test on this level. Move the Level switch to position 3 (right-most position when looking at the switch) and repeat the Record Messages test a third time.

Passing this test means that the Level switch consistently switches between levels, and allows you to record and preview messages on the different levels.

### Message Playback

Slide the Mode switch so it is closest to the assistive switch jacks (Next and Select), and slide the Level switch to the first position. One at a time, press each message button and listen to the playback. Once the message has played back, move on to the next button. Repeat this with all message buttons and on all three levels.

Passing this test means:

- The correct LED lights up and stays on while a message is playing
- Each message plays back when the button is pressed

## MAKER GUIDE

Files available at https://github.com/makersmakingchange/Chatterbox | Page 101 of 103

### Switch Scanning

Plug an assistive switch into each of the assistive switch ports. Press the switch connected to the Select port to start switch scanning and complete each of the following:

1. Allow the Chatterbox to go through all messages.
2. Select a message to playback by pressing the Select switch again
a. While a message is playing.
b. During the delay between messages.
3. Advance through the messages by pressing the switch connected to the Next port
a. While a message is playing.
b. During the delay between messages.

Passing this test means that while a message is playing and during the delay between messages, only the corresponding LED is lit, and it turns off when the next message is played. Additionally:

1. The Chatterbox stops cycling through messages if it advances past the fourth message on the level (whether from pressing the Next switch or going past the delay).
2. The Chatterbox replays the current message when the Select switch is pressed again.
a. The message playing stops and restarts.
b. The message replays.
3. The Chatterbox advances one message when the switch connected to the Next port is pressed.
a. The message stops playing and advances to the next.
b. The next message starts playing.

### Next Switch

While not actively switch scanning, the Next switch has no function. Press the assistive switch connected to the Next port while not switch scanning.

Passing this test means nothing happens when the Next switch is activated if the Chatterbox is not currently switch scanning.

### Speed Switch

Check that changing the position of the Speed switch changes the delay between messages when switch scanning. Move the Speed switch to the middle position (2) and press the Select switch. Let the messages advance automatically, comparing the delay between a message finishing playing and the next starting. Repeat this after changing the Speed switch to the last position (right-most when looking at it).

Passing this test means the length of the delay between messages increases with increasing Speed position. At the time of writing, the default delay times are 3, 5, and 7 seconds for Speeds 1, 2, and 3, respectively.

## MAKER GUIDE

Files available at https://github.com/makersmakingchange/Chatterbox | Page 102 of 103

### Volume

Test that turning the volume knob changes the volume of the messages. Play a message, and while it is playing, turn the volume knob clockwise, then counterclockwise.

Passing this test means the volume increases when turning the knob clockwise, and decreases when turning it counterclockwise.

### Troubleshooting

Below are some potential common issues and how to solve them. If you have any issues with the Chatterbox that are not solved through this troubleshooting, please add them as an Issue to the Chatterbox GitHub repository.

### When powered, the first two lights start blinking and nothing else will happen

This is an error state from the micro-SD card reader not finding a micro-SD card.

1. Double check that the micro-SD card has been inserted properly into the micro-SD card reader.
2. Double check the format of the micro-SD card. The micro-SD card reader requires the card to be formatted in FAT16 or FAT32. The Adafruit website for the micro-SD reader (https://learn.adafruit.com/adafruit-micro-sd-breakout-board-card-tutorial/formatting-notes) has detailed instructions on how to reformat the micro-SD card, if needed.
3. If you used/purchased a different micro-SD card than in the Bill of Materials, double check the size of the card. Windows sets an artificial limit on the size of memory it will format as FAT32 to 32GB. While FAT32 can work on data storage up to 2TB, a Windows system will not allow you to format anything above 32GB as FAT32 without bypassing this artificial limit.

### Chatterbox does not turn on with battery, but did on USB-C power

This is likely due to a dead battery, or bad solder connections for the battery or power

1. Double check if messages play back when a button is pressed, or if LEDs blink when in Record mode. No visible lights turn on while in Playback mode.
2. Replace the battery.
3. Double check solder connections for the battery cap, and power switch on the Secondary PCB.

### An LED does not turn on

This is likely due to a bad connection between the LED PCB and Secondary PCB.

1. Check the solder connections on each PCB.
2. Check that the LED was connected in the correct orientation.
3. Check that the LED has not broken.

## MAKER GUIDE

Files available at https://github.com/makersmakingchange/Chatterbox | Page 103 of 103

### When a button is pressed, the corresponding LED turns on very briefly but nothing else happens

This is likely due to there not being a message recorded for that button.

1. Put the Chatterbox in Record mode and record a message on the corresponding button.

### The Chatterbox seems to skip playing a message while switch scanning, and goes right to the delay between messages

This is likely due to there not being a message recorded for that button.

1. Put the Chatterbox in Record mode and record a message on the corresponding button.

### Nothing happens when I press a message button

This may be due to the button cap not being seated correctly, or issues with the connection between the tactile switch and Main PCB.

1. Remove the button cap and try pressing the switch. If the switch works without the button cap, reposition the button cap and screw it back on.
2. Check the solder joints on the Main PCB and the tactile switch for that button.
3. Check the tactile switch is working.

### Nothing happens when I press the assistive switch attached to the Select jack

This may be due to the switch not working, a bad connection on the Main PCB, or being in the wrong mode.

1. Check that the Chatterbox is powered on and in Playback mode.
2. Check that the assistive switch is working properly.
3. Check the solder connections on the Main PCB.

### Nothing happens when I press the assistive switch attached to the Next jack

The Next jack only works while switch scanning, so if it does not do anything when pressed and you are not switch scanning, that is fine. If you are switch scanning and pressing the Next button does nothing, it may be due to the assistive switch not working, or a bad connection on the Main PCB.

1. Start switch scanning by pressing the switch connected to the Select jack, then press the switch connected to Next again.
2. Check that the assistive switch is working properly.
3. Check the solder connections on the Main PCB.

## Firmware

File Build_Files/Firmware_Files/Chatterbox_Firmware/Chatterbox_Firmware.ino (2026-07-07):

/* 
* File: Chatterbox_Firmware.ino
* Developed by: MakersMakingChange
* Version: v1.0 (13 November, 2025)
  License: GPL v3.0 or later

  Copyright (C) 2025 Neil Squire Society
  This program is free software: you can redistribute it and/or modify it under the terms of
  the GNU General Public License as published by the Free Software Foundation,
  either version 3 of the License, or (at your option) any later version.
  This program is distributed in the hope that it will be useful, but WITHOUT ANY WARRANTY;
  without even the implied warranty of MERCHANTABILITY or FITNESS FOR A PARTICULAR PURPOSE.
  See the GNU General Public License for more details.
  You should have received a copy of the GNU General Public License along with this program.
  If not, see <http://www.gnu.org/licenses/>

<<<<<<<< HEAD:Build_Files/Firmware_Files/Chatterbox_Firmware/Chatterbox_Firmware.ino
  The Chatterbox is an assistive device for augmented and alternative communication (AAC). Users can record messages on each button, 
  then use external switches plugged into 3.5 mm mono jacks to switch scan through the message options. There are also holders for 
  images that a user can place behind each button to represent the message recorded on that button.
========

  November 13, 2025
  Stephan Dobri

  Components:

  Direct access message buttons
  Mode slide switch
  Delay slide switch
  Level slide switch
  3.5 mm mono jacks
  Message LEDs
  Power slide switch
  Volume potentiometer

  Microphone and Amp
    MAX9814        Seeeduino Nano
      GND -----------> GND
      VDD -----------> 5V 
      Out -----------> A0

  Micro SD Breakout Board
    SD Module       Seeeduinon Nano
      5V  -----------> 5V
      GND -----------> GND
      CLK -----------> SCK (D13)
      DO  -----------> MI (D12)
      DI  -----------> MO (D11)
      CS  -----------> SS (D10)

  Audio Amp: PAM8302A
    Amp Module       Seeeduino Nano
      GND -----------> GND
      Vin -----------> 5V
      SD  -----------> D11
      A-  -----------> GND 
      A+  -----------> D9 (Through Vol Pot)
      +   -----------> Speaker postive
      -   -----------> Speaker negitive
  
*/

// Add libraries
//-----------------------------------------------------------------------------------
#include <TMRpcm.h>  // Message recording and playback library
#include <SD.h> // SD card library
#include <SPI.h>
#include <StateMachine.h> // Library for running state machines
#include <neotimer.h> // Timer library for use with state machine library

// Debugging line
#define DEBUG

// Define library variables
//-----------------------------------------------------------------------------------
TMRpcm audio; // Set the variable for playing and recording messages
File myFile; // Set variable for calling the file to play or record
Neotimer delayTimer; // Set timer for the delay between advancing messages without an input
Neotimer recordTimer; // Set timer for when to go from just replaying a message to recording it

// Declare state machine and states
//-------------------------------------------------------------------------------------
StateMachine play_machine = StateMachine(); // Declare the state machine

State* S0 = play_machine.addState(&waiting); // State for when waiting for an input
State* S1 = play_machine.addState(&play_message); // State for playing a message
State* S2 = play_machine.addState(&record_waiting); // State for when waiting for an input to record a new message
State* S3 = play_machine.addState(&record_message); // State for when we're recording a message

//Additional Arduino connections
//----------------------------------------------------------------------------------------
const int mic {A0}; // Pin connected to the mic
const int switch_advance_button {2}; // Button to advance to the next message when switch scanning
const int switch_scan_button {7}; // Button to start switch scanning/select a message
const int speaker_shutdown {8};
const int mode_ID {A5}; // analog input pin to read if it's in playback or recording mode
const int level_ID {A6}; // analog input pin to read which level is selected
const int speed_ID {A7}; // analog input pin to read which playback speed is selected
unsigned int current_message_LED = 0; // LED that will light up or blink for messages, etc.

const int message_buttons[5] = {3, 4, 5, 6, 7}; // Array for the switch pins on the microcontroller.
// The first four spots are for the direct message buttons, and the last is for the switch scanning button.

const int message_LEDs[4] = {A1, A2, A3, A4}; // Array for the message LED pins to the microcontroller.

// Declare variables
//-----------------------------------------------------------------------------------------

//%%%%%%%%%%%%%%%%%%%%%%%%%%%%%%%%%%%%%%%%%%%%%%%%%%%%%%%%%%%%%%%%%%
// Variables a user might want adjusted
const long delay_intervals[3] = {2000, 4000, 6000}; // Set how long the delay is between playbacks, in ms.
const long blinkInterval = 500; // Set the interval of blinking LEDs, in ms
unsigned long record_interval = 1000; // Set how long someone has to hold a button to start recording on it, in ms.
const int volume_value = 5; // Setting volume level, can be 0 to 7. Value of 5 found through trial and error (if set too high the speaker will not play, too low and it won't be audible)
//%%%%%%%%%%%%%%%%%%%%%%%%%%%%%%%%%%%%%%%%%%%%%%%%%%%%%%%%%%%%%%%%%%

// Timing variables
unsigned long previousMillis = 0; // Variable for timing LED blinking
unsigned long currentMillis = 0; // Variable for timing LED blinking
const unsigned long debounce_delay = 50; // Debouncing delay time, in ms

//File properties
int file_number = 0; // Variable for which file will be recorded or played
int file_level {1}; // Variable for which level is selected
int current_message {1}; // Variable to store which message number is being played or recorded
const int sample_rate {16000}; // Sampling rate for the mic when recording messages
const int message_total = 3; // Indexing variable for the last position in the message array (3 is the fourth message, as indexing starts at 0).
int LEDState = LOW; // Variable for turning LEDs on or off
int which_switch = -1; // Variable to identify which of the switches have been hit for playing back or recording messages.
// Hard code in the file variable name
char file_ends[][7]{"_1.wav", "_2.wav", "_3.wav", "_4.wav"}; // Ending of the file names the Chatterbox records / recognizes
char file [12]; // Variable to call the file to record or play back

// Other variables
const int playback_threshold = 510; // variable for checking the threshold to be in playback vs record mode
const int threshold[2] = {300, 510}; // Variable for checking the level to run and changing delay between messages based on the ouptut of a resistor ladder

// Boolean values for triggering transitions
//-----------------------------------------------------------------------------------------------------

struct Flags {
  bool advance_message : 1; // Stop playing a message and move to the next
  bool switch_scanning : 1; // Indicate if in switch scanning or playing a message directly
  bool recording_mode : 1; // Indicate if in recording or switch scanning mode
  bool record_a_message : 1; // Transition to recording a message
  bool record_playback : 1; // Playback a message from the recording mode
  bool first_loop : 1; // Indicate if it's the first time through a loop
  // Add more flags here
};
Flags flags;

bool play_transition[2] = {false, false}; // Tracks the state of messages playing. It stores the previous state (false for not playing, true for playing) and can compare that to the current state.

//------------------------------------------------------------------------------------------------------
// Functions

// Blink single LED function

void blink_LED(){
  currentMillis = millis();

  if(currentMillis - previousMillis >= blinkInterval){
    previousMillis = currentMillis;

    if(LEDState == LOW){
      LEDState = HIGH;
    }
    else{
      LEDState = LOW;
    }
    digitalWrite(current_message_LED, LEDState);
  }
}

// Blink all LEDs function. Used when in record mode.

void blink_all_LEDs(){
  currentMillis = millis();

  if(currentMillis - previousMillis >= blinkInterval){
    previousMillis = currentMillis;

    if(LEDState == LOW){
      LEDState = HIGH;
    }
    else{
      LEDState = LOW;
    }
    digitalWrite(message_LEDs[0], LEDState);
    digitalWrite(message_LEDs[1], LEDState);
    digitalWrite(message_LEDs[2], LEDState);
    digitalWrite(message_LEDs[3], LEDState);
  }
}

// Check and set the level the messages are on
char check_level(){

  if(analogRead(level_ID) <= threshold[0]){ // Check if resistor ladder reading is below the first threshold value
    strcpy(file,"rec_1"); // Set the first part of the file variable for being in Level 1
    strcat(file,file_ends[file_number]); // Append the endings of the file numbers
    return file;
  }
  else if(analogRead(level_ID) >= threshold[1]){ // Check if resistor ladder reading is above the second threshold value
    strcpy(file,"rec_3"); // Set the first part of the file variable for being in Level 3
    strcat(file,file_ends[file_number]); // Append the endings of the file numbers
    return file;
  }
  else{ // Last remaining option where the resitor ladder reading is between the two threshold values
    strcpy(file,"rec_2"); // Set the first part of the file variable for being in Level 2
    strcat(file,file_ends[file_number]); // Append the endings of the file numbers
    return file;
  }
}

// Check and set the delay between advancing to the next message while switch scanning
// This function works exactly as the check_level function, but sets the delay value
long check_delay_duration(){
  if(analogRead(speed_ID) <= threshold[0]){
    return delay_intervals[0];
  }
  else if(analogRead(speed_ID) >= threshold[1]){
    return delay_intervals[2];
  }
  else{
    return delay_intervals[1];
  }
}

// Checking memory function for debugging. Output free RAM in bytes.

extern int __heap_start, *__brkval;
int freeMemory() {
  int v;
  return (int)&v - (__brkval == 0 ? (int)&__heap_start : (int)__brkval);
}

//------------------------------------------------------------------------------------------------------
// States of state machine
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

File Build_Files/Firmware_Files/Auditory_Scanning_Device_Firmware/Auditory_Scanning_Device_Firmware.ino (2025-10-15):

/* 
* File: Chatterbox_Firmware.ino
* Developed by: MakersMakingChange
* Version: v1.0 (02 February 2024)
  License: GPL v3.0 or later

  Copyright (C) 2025 Neil Squire Society
  This program is free software: you can redistribute it and/or modify it under the terms of
  the GNU General Public License as published by the Free Software Foundation,
  either version 3 of the License, or (at your option) any later version.
  This program is distributed in the hope that it will be useful, but WITHOUT ANY WARRANTY;
  without even the implied warranty of MERCHANTABILITY or FITNESS FOR A PARTICULAR PURPOSE.
  See the GNU General Public License for more details.
  You should have received a copy of the GNU General Public License along with this program.
  If not, see <http://www.gnu.org/licenses/>

<<<<<<<< HEAD:Build_Files/Firmware_Files/Open_Playback_Switch_Firmware/Open_Playback_Recorder_Firmware.ino
  The Open Playback Button is an assistive technology device capable of recording voice messages and storing them for future playback.   
  Messages can be recorded after entering record mode by holding the record button for 2 seconds. In record mode, multiple messages can be recorded to a micro SD 
  card by pressing and holding the play button before pressing the record button again to exit record mode. The stored
  messages can then be played back with each press of the play button. An external button can be plugged into a 3.5 mm
  mono jack to act as an accessible play button.  
========

  The Open Playback Button is a device capable of recording voice messages and storing them for future playback.   
  This code will showcase the basic functionality of the device. Messages can be recorded after entering record 
  mode by holding the record button for 2 seconds. In record mode, multiple messages can be recorded to a micro SD 
  card by pressing and holding the play button before pressing the record button again to exit record mode. The stored
  messages can then be played back with each press of the play button. An external button can be plugged into a 3.5 mm
  mono jack to act as an accessible play button.  

  July 25, 2023
  Brad Wellington

  Updating code to work with the new microcontroller and include the 3 levels or recordings

  Components:

  Play button
  Record button
  Volume potentiometer with on/off switch
  play/rec leds
  3.5 mono jack

  Microphone and Amp
    MAX9814        Arduino Uno
      GND -----------> GND
      VDD -----------> 5V 
      Out -----------> A0

  Micro SD Breakout Board
    SD Module       Arduino Uno
      5V  -----------> 5V
      GND -----------> GND
      CLK -----------> SCK
      DO  -----------> MI
      DI  -----------> MO
      CS  -----------> SS

  Audio Amp: PAM8302A
    Amp Module       Arduino Uno
      GND -----------> GND
      Vin -----------> 5V
      SD  -----------> D11
      A-  -----------> GND 
      A+  -----------> D9 (Through Vol Pot)
      +   -----------> Speaker postive
      -   -----------> Speaker negitive
      
  File: Open_Playback_Recorder_Firmware.ino
  Developed by: Makers Making Change
  Version: V2.0(17 July 2024)
  License: GPL v3
  
Copyright (C) 2023-2024 Neil Squire Society
  This program is free software: you can redistribute it and/or modify it under the terms of
  the GNU General Public License as published by the Free Software Foundation,
  either version 3 of the License, or (at your option) any later version.
  This program is distributed in the hope that it will be useful, but WITHOUT ANY WARRANTY;
  without even the implied warranty of MERCHANTABILITY or FITNESS FOR A PARTICULAR PURPOSE.
  See the GNU General Public License for more details.
  You should have received a copy of the GNU General Public License along with this program.
  If not, see <http://www.gnu.org/licenses/>
  
>>>>>>>> PCB-Version:Build_Files/Firmware_Files/Open_Playback_Recorder_Firmware/Open_Playback_Recorder_Firmware.ino
*/

// Add libraries
//-----------------------------------------------------------------------------------
#include <TMRpcm.h>  // Message recording and playback library
#include <SD.h> // Libary
#include <SPI.h>
#include <StateMachine.h>
#include <neotimer.h>

// Debugging line
#define DEBUG

// Define library variables
//-----------------------------------------------------------------------------------
TMRpcm audio;
File myFile;
Neotimer delayTimer; // Set timer for the delay between advancing messages without an input
Neotimer recordTimer; // Set timer for when to go from just replaying a message to recording it
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

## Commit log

2025-05-16 Removing older files and making code more readable
    - Removed old files that weren't necessary when using Git properly (testing different functions, etc.)
    - Updated Firmware file to most current version
    - Removed unnecessary variables/comments
    - Rearranged code and added more comments to make it more readable
2025-05-21 Update Auditory_Scanning_Device_Firmware.ino
    Working on troubleshooting current issues where messages don't play with added functions.
2025-06-04 Memory use optimization
    - Optimized parts of code for memory use
    - Implemented arrays to get rid of magic numbers for buttons and LEDs
    - Added in (mostly) empty states and transitions for all states and transitions required
    - Added firmware log file for tracking work and productivity
2025-06-20 Added message recording and playback functionality.
    - Added message recording and playback from recording mode.
    - Added code to turn off all LEDs in various places to remove edge cases where LEDs stayed on.
2025-07-10 Log update and testing output of resistor ladders
    - Removed old comments
    - Added testing for the output of the resistor ladders
    - Added threshold variables for the level, speed, and playback vs record
2025-10-15 Adding build files
    Added STL and Gerber files for building the device.
    [Battery_Holder.stl, Button_Base.stl, Button_Cap_Insert.stl, Button_Cap_Plain.stl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]
2025-10-30 Added images and deleted extraneous files.
    [OpenAT_Placard.stl]
2025-11-13 Cleaning up and commenting firmware
    - Removed vestigial variables and code snippets
    - Added more comments to increase readability
    - Updated descriptions of the firmware/device that referenced the Open Playback Recorder still
2025-11-18 Updated STL files
    Updated STL files with minor changes from previous commit.
    [Battery_Cover.stl, Battery_Holder.stl, Button_Cap.stl, Button_Insert.stl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]
2025-11-26 Updated STL and Gerber files
    - Updated STL files to include branding
    - Updated/corrected PCB labels to V1.0
    [Enclosure_Bottom_Left.stl, Enclosure_Top_Left.stl, Enclosure_Top_Right.stl]
2025-12-17 Updated PCB files, removed log file
    - Updated PCB zip files
    - Removed log file that was being used to track progress in Chatterbox firmware
2025-12-17 U[dated files
    - Updated print orientation of button cap
    - Added CSV for BOM
    - Removed template guide file
    [Button_Cap.stl, Chatterbox_BOM.csv]
2026-01-09 Update documentation and design files
    Updated documentation:
    - Added documents in Word and PDF format
    Added design files:
    - Added Fusion 360 file for the enclosure and the PCBs
    [Chatterbox_BOM.xlsx, Device_Name_BOM.xlsx, OpenAT_Placard.f3d]
2026-02-17 Updated files with OSHW certification number
    - Updated PCB and enclosure files to include the OSHW certification number
    - Updated stl files for shorter version of Chatterbox
    [Battery_Cover.stl, Button_Base.stl, Button_Cap.stl, Button_Insert.stl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]
2026-02-19 Added STLs for switch covers and updated design files
    - Added STL files for the switch cover and pin
    - Updated PCB and CAD design files
    [LED_PCB.f3z, Secondary_PCB.f3z, Slide_Switch_Cover.stl, Slide_Switch_Cover_Pin.stl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]
2026-02-25 Updated depth of screw holes for LED PCBs
    Updated length of screw posts for LED PCBs so tip of screw does not mark enclosure top.
    [Enclosure_Top_Left.stl, Enclosure_Top_Right.stl]
2026-03-13 Updated PCB Gerber files and design files
    Updated PCB Gerber and design files to final version.
    [Secondary_PCB.f3z]
2026-03-19 Added cutout for slide switch pins
    - Added cutouts for slide switch pins to the enclosure body
    - Cutouts were needed for the power and mode switches
    [Battery_Cover.stl, Enclosure_Bottom_Left.stl, Enclosure_Top_Left.stl, Enclosure_Top_Right.stl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]
2026-03-26 Updated documentation
    Updated all documentation in our regular package (except the Design Rationale).
    [Chatterbox_BOM.csv, Chatterbox_BOM.xlsx]
2026-04-15 Fix mono speaker BOM link to correct DigiKey part
    [Chatterbox_BOM.csv, Chatterbox_BOM.xlsx]
2026-04-15 Replace out-of-stock slide switches in BOM
    [Chatterbox_BOM.csv, Chatterbox_BOM.xlsx]
